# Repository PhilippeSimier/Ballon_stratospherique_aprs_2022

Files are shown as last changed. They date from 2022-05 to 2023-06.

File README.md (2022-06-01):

# Ballon sonde stratosphérique

## Objectifs pédagogiques
La  construction d'une nacelle expérimentale de ballon doit permettre aux jeunes, une découverte des sciences expérimentales. Les expériences  mettent en oeuvre la mesure de grandeurs physiques avec la transmission des données par radiofréquence.  Une initiation à la démarche de projet est aussi proposée.

## Introduction
 L'objectif  est de faire de la science afin de pouvoir mieux comprendre notre atmosphère jusqu’à 30 km d’altitude. Nous tenterons de répondre à la question suivante :

 - Dans quelle mesure l'atmosphère nous protège t-elle du [rayonnement cosmiques](https://www.sievert-system.org/#Rayonnement)   ?

Le rayonnement cosmique est formé de particules qui se déplacent à une vitesse proche de celle de la lumière. Il est constitué de deux composantes, l’une stable, d’origine galactique, l’autre plus fluctuante, liée à l’activité du soleil.
Pour le comprendre, commençons par l'espace lointain. Les rayons cosmiques sont essentiellement des débris subatomiques d'étoiles mourantes, accélérés à une vitesse proche de la lumière par des explosions de supernova. Ils voyagent à travers l'espace et s'approchent de la Terre
dans toutes les directions, bombardant notre planète 24h/24 et 7j/7.
Lorsque les rayons cosmiques s'écrasent dans l'atmosphère terrestre, ils produisent un jet de particules secondaires et de photons qui est le plus intense à l'entrée de la stratosphère. Les physiciens Eric Regener et Georg Pfotzer ont découvert ce maximum en utilisant des ballons dans les années 1930 et c'est ce que nous allons vérifier aujourd'hui.

|Altitude (m)|  Débit de dose (μSv/h)|
|--|--|
|80  | 0.08 |
|5000  | 1.8 |
|8200  | 4.1 |
|10000  | 5.2 |
|11200  | 7.7 |

 [Unité de mesures](https://www.sievert-system.org/#Mesure)

Lors du vol, le ballon traverse une couche appelée le Regener-Pfotzer Maximum, une couche de rayonnement maximal à environ 20 km au-dessus de la surface de la Terre. Ce graphique de rayonnement en fonction du temps pris lors d'un vol en ballon en juillet 2015 illustre le pic :

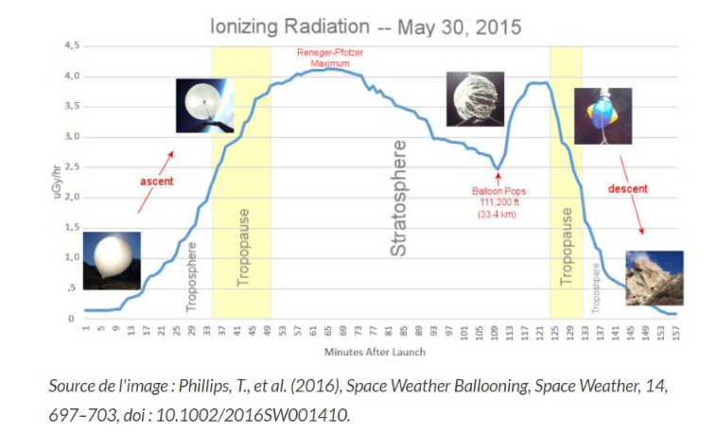
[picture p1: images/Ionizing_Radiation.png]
Ionizing_Radiation


## Principe de la mesure rayonnement ionisant

Le rayonnement est composé de photons gamma et de particules capables de provoquer, directement ou indirectement, la formation d'ions (par arrachement d'électrons) dans la matière qu’ils traversent.

La détection du rayonnement ionisant repose  sur un type particulier de diode, la **diode PIN**. PIN pour Positive Intrisic Negative fait référence directement à la manière dont est constitué le composant.  Dans  une diode PIN on trouve entre les zones P et N une zone non dopée dite intrinsèque.  
La structure PIN permet la détection de photons, un peu à la manière d'un tube Geiger-Muller avec un effet cascade et une brève conductivité. Cela signifie que si un rayon de haute énergie est absorbé, un signal détectable d'électrons est généré. l'absorption photoélectrique est dominante dans la région d'énergie gamma d'intérêt entre 5 keV et 100 keV.
Les détecteurs basés sur **l'absorption directe dans le silicium** constituent une alternative  peu coûteuse par rapport au détecteur à gaz (tube Geiger-Muller).
le capteur utilisé possède une photodiode PIN **[X100-7](https://www.first-sensor.com/cms/upload/datasheets/X100-7_THD_5000040.pdf)** pour la détection des rayons ionisants, ayant une surface de section efficace à grande échelle (100 mm ^ 2), fabriquée par la société **FirstSensor** qui a également fourni un capteur similaire pour le télescope à rayons X de la NASA. En règle générale, l'efficacité du capteur à photodiode PIN est extrêmement stable et ne présente aucune dégradation liée à l'âge.
La détection et l’électronique qui l'entoure est là pour amplifier le signal et le transmettre avec des niveaux adaptés vers un entrée digital de l'ESP32. On obtient le débit de dose par comptage des impulsions sur une periode donnée.

### Principe
Le ballon s’élève dans l’atmosphère grâce à la **poussée d’Archimède**. Plus il monte, plus la pression de l’air autour de lui, diminue. L’hélium occupe alors de plus en plus de volume : le ballon se dilate et finit par éclater.

A ce moment, la chaîne de vol redescend vers la terre. Le parachute inséré initialement «  en sapin  » entre l’enveloppe du ballon et le réflecteur radar, joue alors son rôle de frein.

La durée totale du vol se situe entre 2 et 4 heures. **Planète Sciences** se charge de la demande d’autorisation de vol auprès des autorités. 

### La Nacelle
Pendant le vol, les capteurs seront intégrés dans la Nacelle  qui assurera les fonctions de plate-forme : intégration mécanique, isolation et contrôle thermique, localisation/datation des observations, fourniture de l’énergie grâce à des panneaux solaires et batteries.
La nacelle devra être capable de fonctionner de manière autonome pendant 4 heures, en environnement stratosphérique (pression 50-70 hPa, température environ -80°C).
Les contraintes de masse embarquée sous ballons pressurisés sont telles qu’il est impossible de faire voler une nacelle de plus de 1,8 kg.

### Mécanique 
(design, calculs, atelier, réalisation, intégration) : 
Cette tâche consiste en la conception et la réalisation des coques externes de la  nacelle, ainsi que la structure interne permettant l’intégration des capteurs et des différents sous-systèmes. La structure de la nacelle est réalisée en polystyrène expansé de 30mm d'épaisseur.
La nacelle est recouverte par collage d'une couverture de survie. La colle utilisée est une colle en spray **3M PhotoMount**.

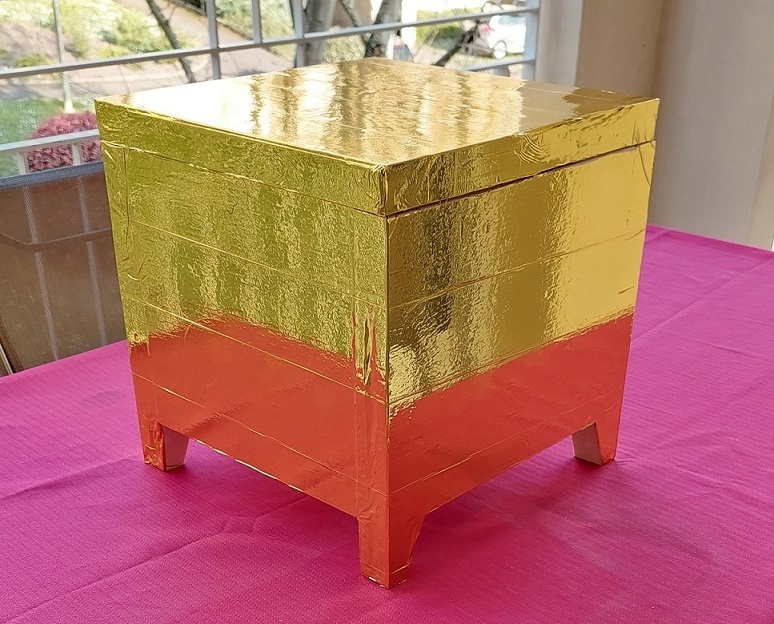
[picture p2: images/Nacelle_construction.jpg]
Nacelle


### Les cartes de télémesures et d'alimentation

L’ensemble des cartes électroniques ont le même format et sont fixées au couvercle. Elles sont ainsi facilement retirables de la nacelle. Les cartes sont empilées  et sont maintenues séparées les unes des autres au moyen de 4 entretoises hexagonales disposées dans les coins. 

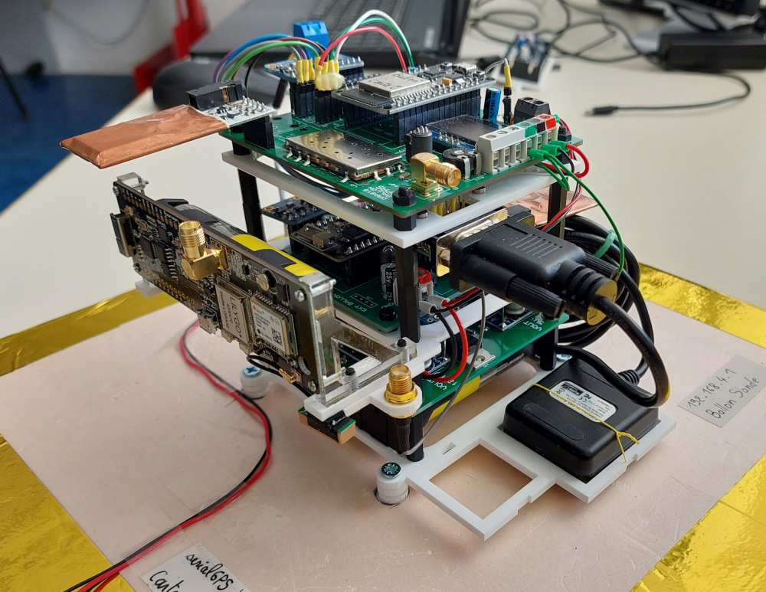
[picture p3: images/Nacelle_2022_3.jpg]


Tout  au  long  du  vol,  les  mesures  sont  enregistrées à bord sur une carte SD. elles  sont aussi envoyées au sol par les émetteurs embarqués (APRS LORA et SIGFOX).

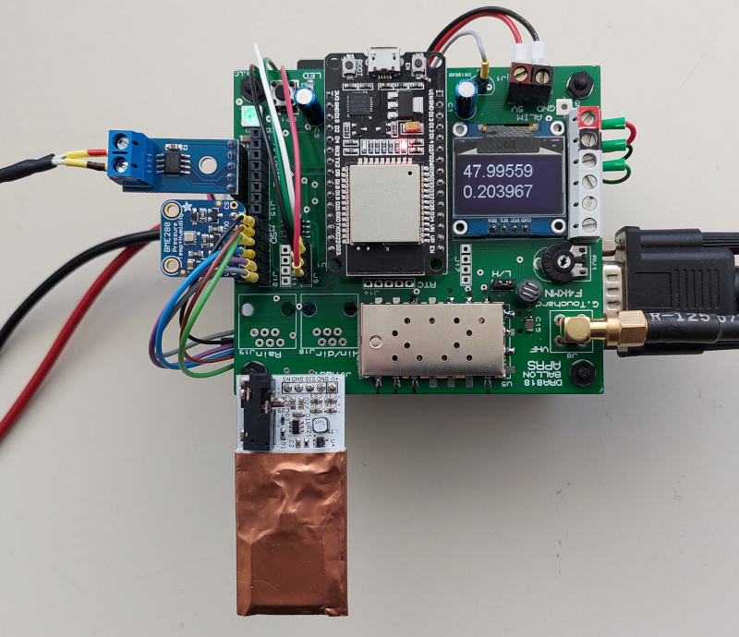
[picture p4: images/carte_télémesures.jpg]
Carte de télémesures


### Le suivi de la trajectoire de vol 

Afin de faciliter la récupération de la nacelle, le système de télémesures est équipé d’un récepteur GPS pouvant fonctionner en haute altitude.
Le suivi du vol est effectué par transmission de la position dans des trames **APRS** encapsulé dans des trames **FX25** et aussi **LoRa**.  
La position est également transmise sur le réseau **SIGFOX**.

La position du ballon ainsi que la télémétrie peuvent être suivie en temps réel sur le site https://aprs.fi/

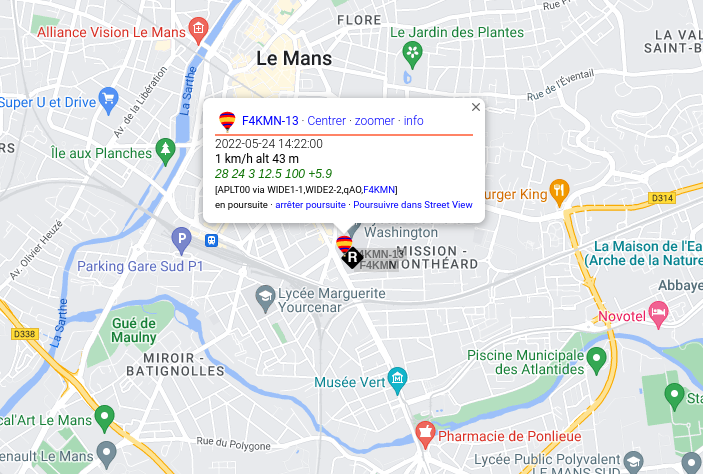
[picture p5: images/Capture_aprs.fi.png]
aprs.fi


ou sur le site https://aprs-map.info/

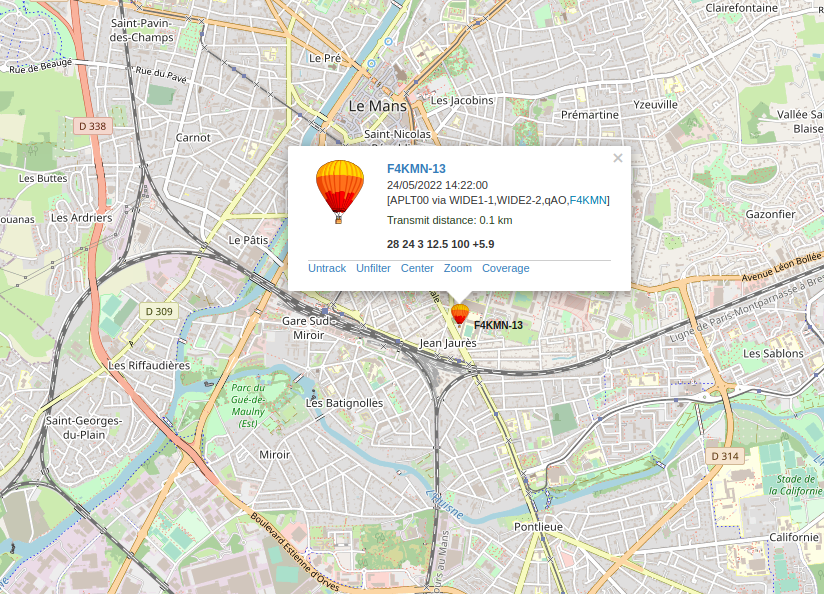
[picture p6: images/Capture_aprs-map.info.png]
aprs-map.info


## La télémétrie

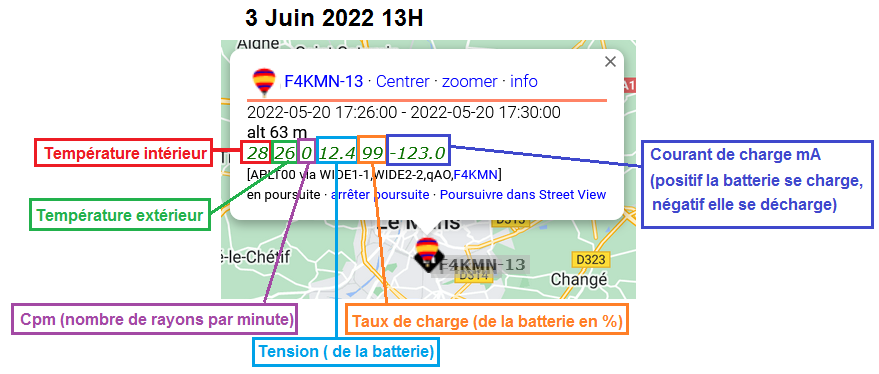
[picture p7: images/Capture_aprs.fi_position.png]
aprs.fi


La télémétrie permet de suivre la charge de la batterie, les températures intérieur et extérieur, le nombre par minute de rayons cosmiques. 

## Les prévisions de trajectoire et météorologiques

[Prévisions de la trajectoire](https://predict.habhub.org/)
[Prévisions météorologiques](https://www.ventusky.com)

Prévision de la trajectoire 48 heures avant le lancement
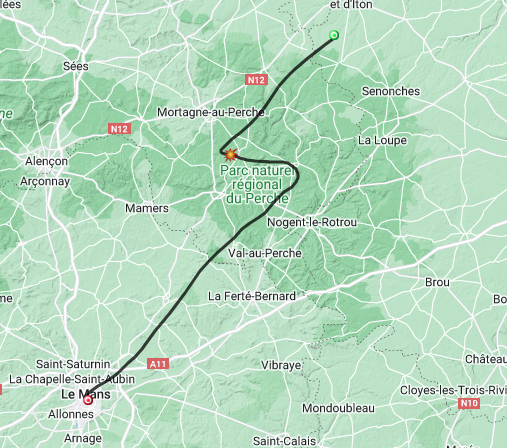
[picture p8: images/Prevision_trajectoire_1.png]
Prévision trajectoire


## Les contraintes

 1. La chaîne de mesure doit être étalonnée dans son intégralité     (système au sol compris) avant le vol.

 2. L'alimentation de la chaîne de mesure doit posséder une autonomie supérieure à 4 heures.

 3. La localisation se fait alors par l'écoute d'une des _fréquences_ utilisées par  _Planète Sciences_ ( 137.05 MHz ).

Section Système Numérique Informatique & Réseaux

Logo Lycée Touchard Logo CNES
Logo Planete sciences

<!-- Toolbox
Génération du README  https://stackedit.io/app#
Génération des badges https://shields.io/category/build

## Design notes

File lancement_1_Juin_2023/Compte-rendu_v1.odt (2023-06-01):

Pesage de la nacelle 1626 g

alimentation

consommation 247mA

Taux de charge de la batterie restant 70 %

tension 11,7 V

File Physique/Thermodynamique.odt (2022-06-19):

## Thermodynamique

Système Nacelle

Travail

W

Transfert thermique
Q

Sources électriques Air ambiant

Variation d’énergie interne du sytème

%DELTA U_système = W +Q

La température interne de la nacelle avant le décollage est constante donc %DELTA U _système = 0

La nacelle est composée de panneau en polystyrène extrudé épaisseur 30mm

Le constructeur donne la résistance thermique pour 1 m² de panneau : 0,90 m²KW⁻¹

Surface intérieure des 6 faces 0,24 * 0,24 * 6 = 0,3456 m²

Rth = 0,90 / 0,3456 = 2,6 KW⁻¹ R_{ th } = {0,90} over {0,3456} = bold 2,6 KW ^{-1}

à 13h43 la nacelle est fermée la température intérieure est constante.

%theta_{i} = 34 °C
%theta_{ext} = 24 °C
%DELTA %theta = %theta_{e} - %theta_{i} = -10 °C

Flux thermique %PHI = {%DELTA %theta} over { R_{th} } = { -10 } over { 2,6 } = bold -3,84 W

Puissance électrique dissipée par les cartes électronique APRS et Sigfox = 12,4 * 0,174 = 2,15 W

Puissance électrique carte ttgo LoRa 4.00V * 102mA = 0,408 W

Puissance électrique GoPro 5V * 250mA = 1,25 W

Total puissance électrique = 3,8 W

Bilan des puissances Pe + flux thermique 3,8 – 3,84 = - 0,04W

Conclusion le bilan des puissances est équilibré

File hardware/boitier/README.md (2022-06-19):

# Conception Mécanique

## Liens utiles

**Conception 3D** 

https://www.tinkercad.com/dashboard

**Converter svg to dxf**

https://cloudconvert.com/svg-to-dxf

**Viewer dxf de autodesk**

https://viewer.autodesk.com/designviews

# Assemblage nacelle

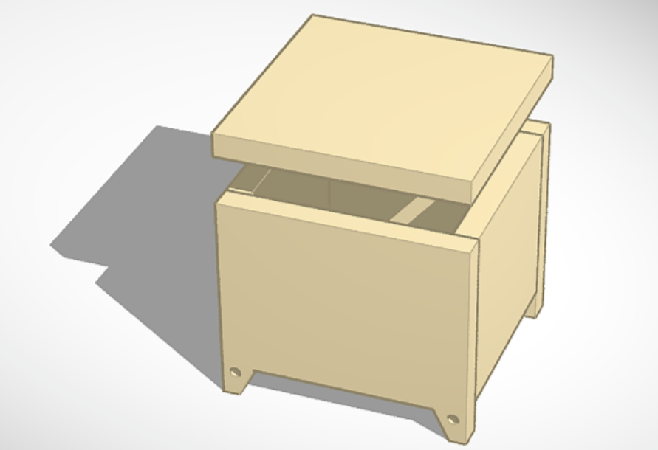
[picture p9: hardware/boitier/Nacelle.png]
Assemblage nacelle


# Les piéces mécaniques

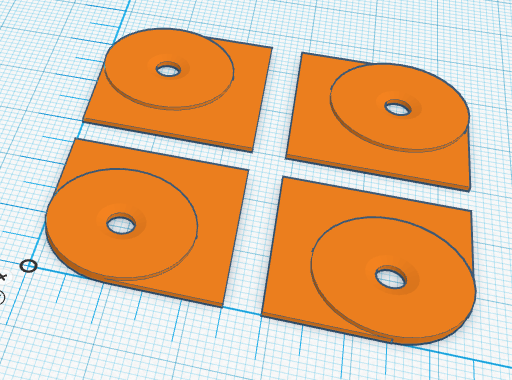
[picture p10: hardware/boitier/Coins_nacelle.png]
coins nacelle


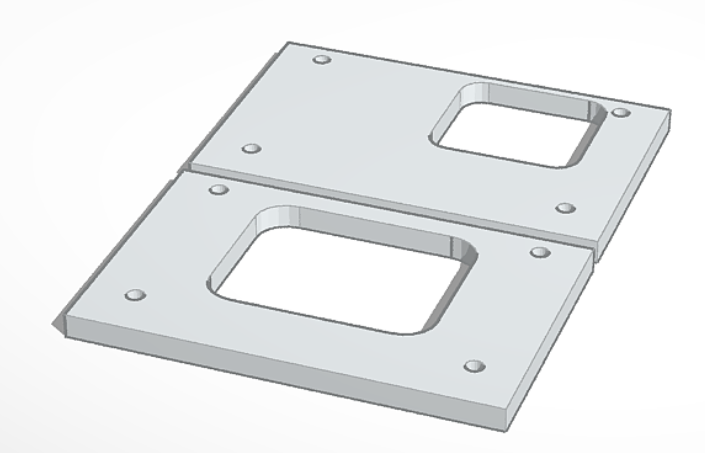
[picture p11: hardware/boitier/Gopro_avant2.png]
Gopro_avant2


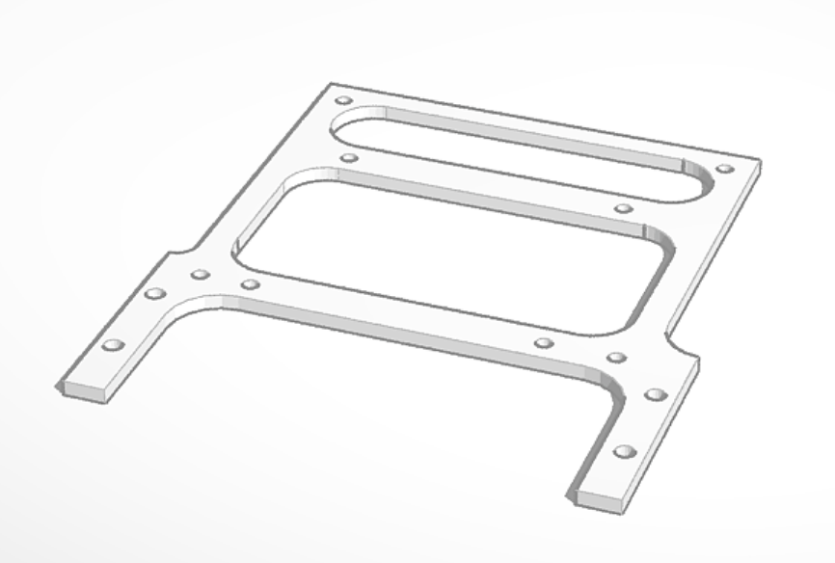
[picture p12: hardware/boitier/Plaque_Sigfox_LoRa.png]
Plaque_Sigfox_LoRa


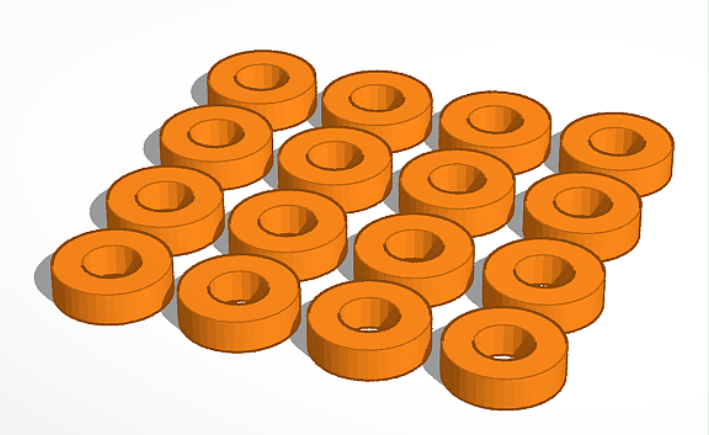
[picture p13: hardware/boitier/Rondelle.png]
Rondelle


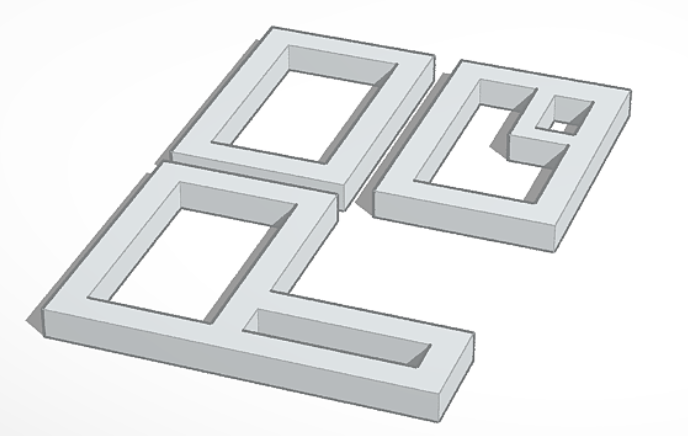
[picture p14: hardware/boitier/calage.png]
calage


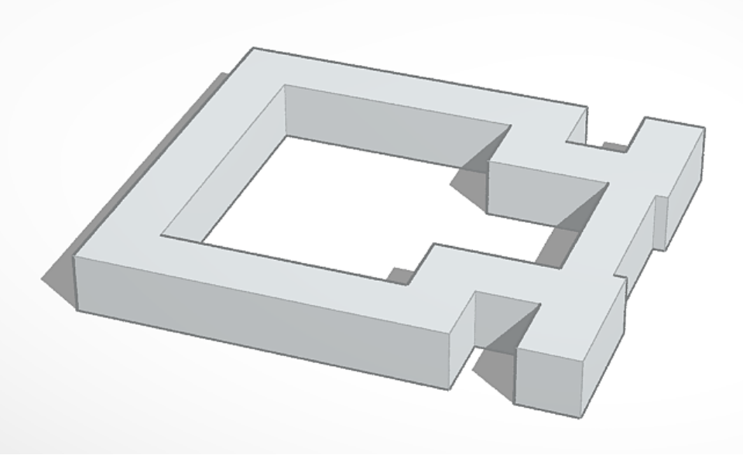
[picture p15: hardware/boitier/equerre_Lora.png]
équerre LoRa


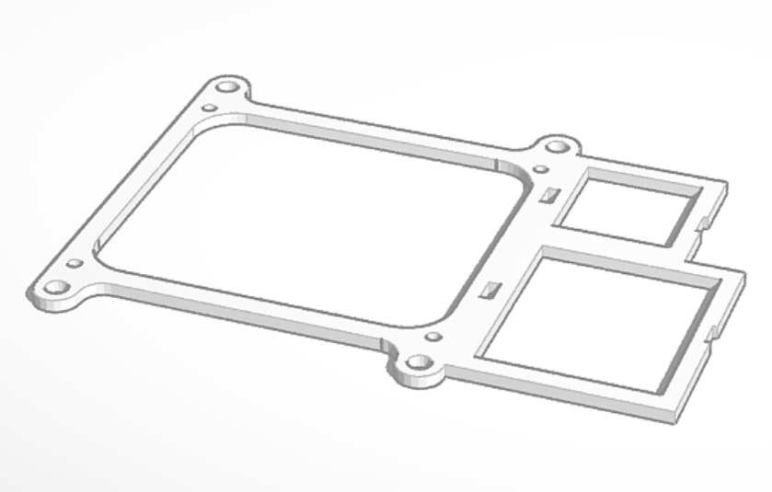
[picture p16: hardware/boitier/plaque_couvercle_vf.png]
plaque couvercle


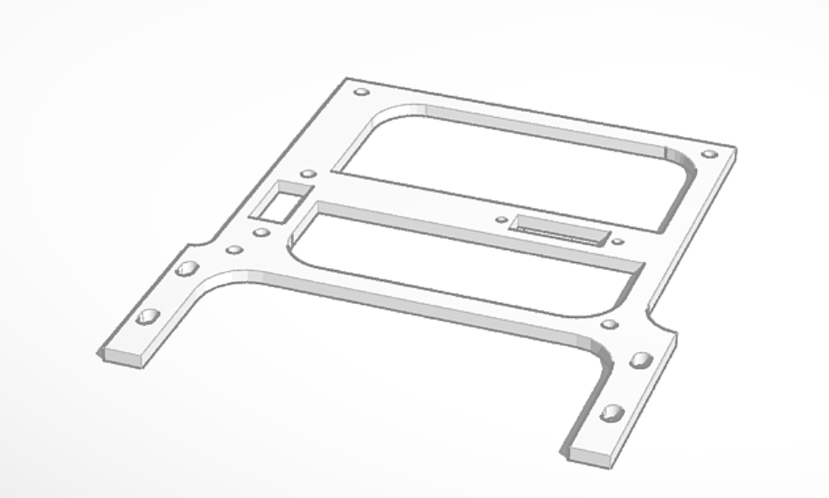
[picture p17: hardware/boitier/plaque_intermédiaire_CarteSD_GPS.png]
plaque carte SD & GPS


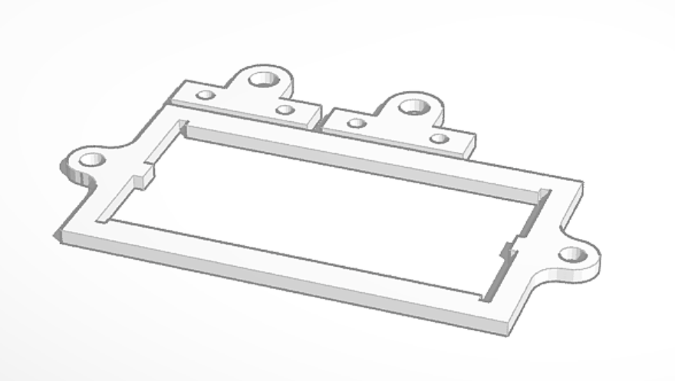
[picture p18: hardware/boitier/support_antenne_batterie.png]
support antenne batterie gopro


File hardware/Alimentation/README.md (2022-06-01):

# Génération d'énergie

## Objectif

La  _génération d'énergie_  permet le fonctionnement de la nacelle en lui fournissant l'énergie électrique dont elle a besoin. En effet, cette dernière étant mobile et autonome, elle a besoin de produire son électricité. Le système d'alimentation électrique est découpé en quatre éléments qui sont la production (ou **source primaire**), le stockage (ou **source secondaire**), la régulation et la distribution.

-   La production électrique utilise  le flux solaire grâce à des panneaux solaires placés sur les côtés de la nacelle.  Des cellules solaires assurent la conversion de l'énergie lumineuse en énergie électrique, avec un certain rendement entre 20 et 30% . 
-   L'énergie produite est ensuite stockée dans les batteries 18650 (lithium ion) afin d'alimenter la nacelle lors des phases  ou la consommation instantanée est supérieure à la production des panneaux.
-   La régulation et la distribution permettent de fournir aux éléments nécessitant de l'énergie une alimentation présentant des caractéristiques électriques précises et compatibles. La régulation permet de garantir la durée de vie de la batterie. Pour ce faire, on limite la profondeur de décharge, c'est-à-dire la quantité d'énergie fournie par la batterie.
- Par ailleurs on coupe le courant de charge lorsque la température intérieure dans la nacelle est inférieur à 0°C.

## Schéma

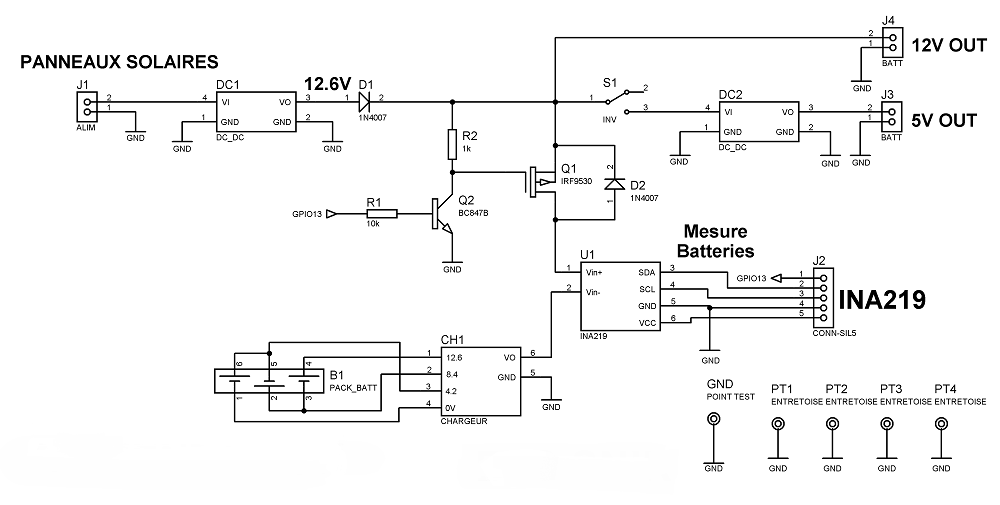
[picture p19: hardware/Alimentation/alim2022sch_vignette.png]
schema alimentation
 

 ## PCB
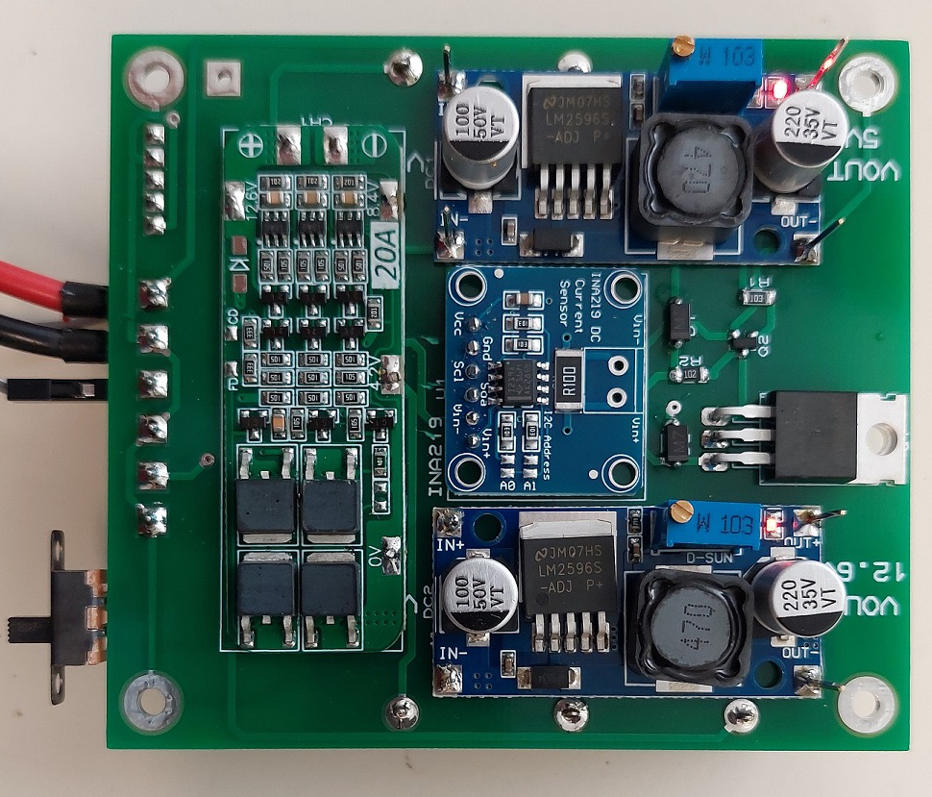
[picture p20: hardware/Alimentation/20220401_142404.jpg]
carte coté composants
 

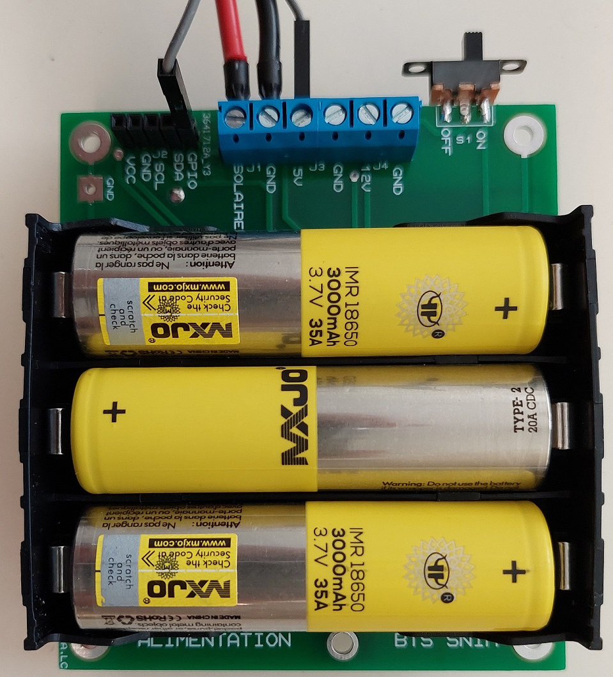
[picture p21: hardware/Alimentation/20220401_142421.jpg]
carte coté batteries


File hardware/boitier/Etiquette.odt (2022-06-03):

Cet objet est inoffensif.

Il est la propriété du

Cet objet est la concrétisation d'un projet d'élèves. Nous sommes en route pour le récupérer.

Si vous le trouvez merci d'appeler le :

07 68 12 72 54

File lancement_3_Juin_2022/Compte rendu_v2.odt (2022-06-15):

# Ballon stratosphérique Lycée Touchard Washington

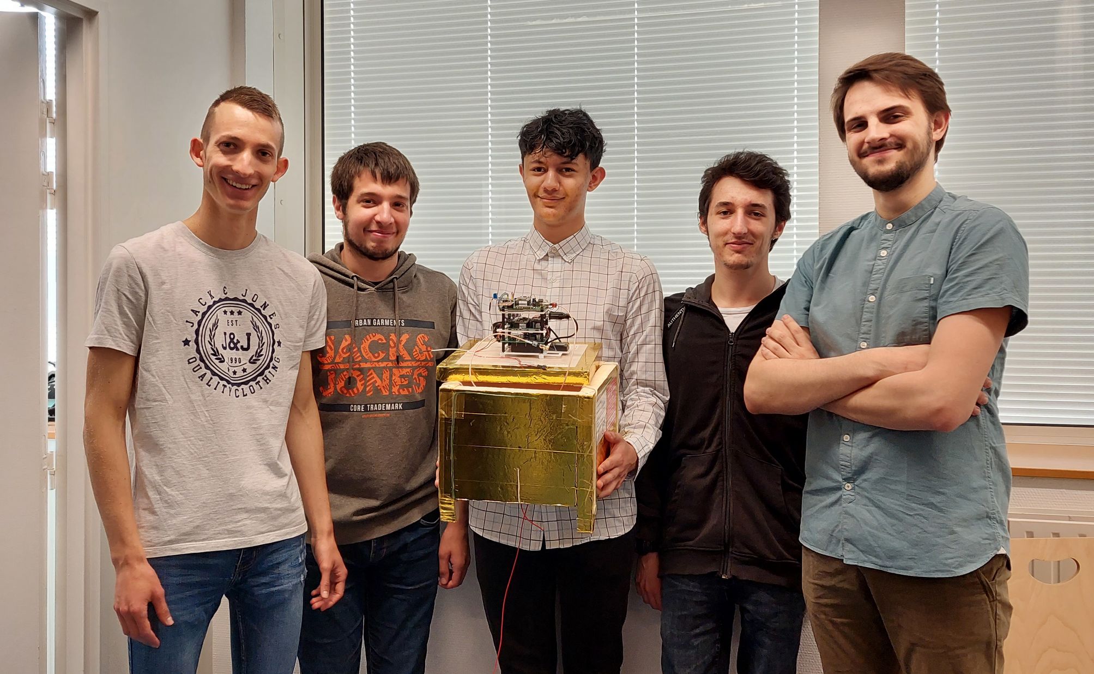
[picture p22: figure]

Desaunay Valentin, Neveu Benjamin, Suard Mickael , Maillard Clement, Porcheron Enzo

Professeurs référents : Bernard Didier, Le Cren Anthony, Simier Philippe

# Bilan des mesures Ballon 2022

### Présentation générale

Le projet de ballon stratosphérique 2022, fut réalisé par 5 étudiants dans le cadre du projet de deuxième année du BTS Système numérique option informatique, durant l'année scolaire 2021-2022. Les idées motivant sa réalisation étaient la mesure de la radioactivité en altitude et l'utilisation d'un capteur GNSS pour suivre la position du ballon, et donc le récupérer. Le ballon a été lancée le 3 juin 2022 depuis Le Mans (72), suivi par une voiture et retrouvé quelques minutes après son atterrissage. Malgré quelques problèmes, les résultats des expériences ont pu être exploités avec intérêt.

### Pesée - Vitesse de montée - Altitude d’éclatement

Le ballon s’élève dans l’atmosphère grâce à la poussée d’Archimède. Plus il monte, plus la pression de l’air autour de lui, diminue. L’hélium occupe alors de plus en plus de volume : le ballon se dilate et finit par éclater.

A ce moment, la chaîne de vol redescend vers la terre. Le parachute inséré initialement « en sapin » entre l’enveloppe du ballon et le réflecteur radar, joue alors son rôle de frein.

Masse de la nacelle : 1455 g.

Nous sommes en dessous des 1800 g exigé par le cahier des charge. Le gonflage du ballon a été adapté (5,1 m³ d’hélium) afin d’avoir la portance qui permette une vitesse ascensionnelle de 5 m/s.

Vitesse ascensionnelle décollage = 4,74 m/s

Vitesse ascensionnelle à 4000 m = 5,21 m/s

Vitesse ascensionnelle à 20000 m = 5,41 m/s

Vitesse ascensionnelle à 30000 m = 6,57 m/s

Altitude à l’éclatement = 34 295 m

Les années précédentes la nacelle était plus lourde (1800g) le ballon était donc gonflé avec un volume d’hélium plus important et éclatait vers 30 000m. Conclusion , un ballon contenant moins d'hélium éclate à une altitude plus élevée.

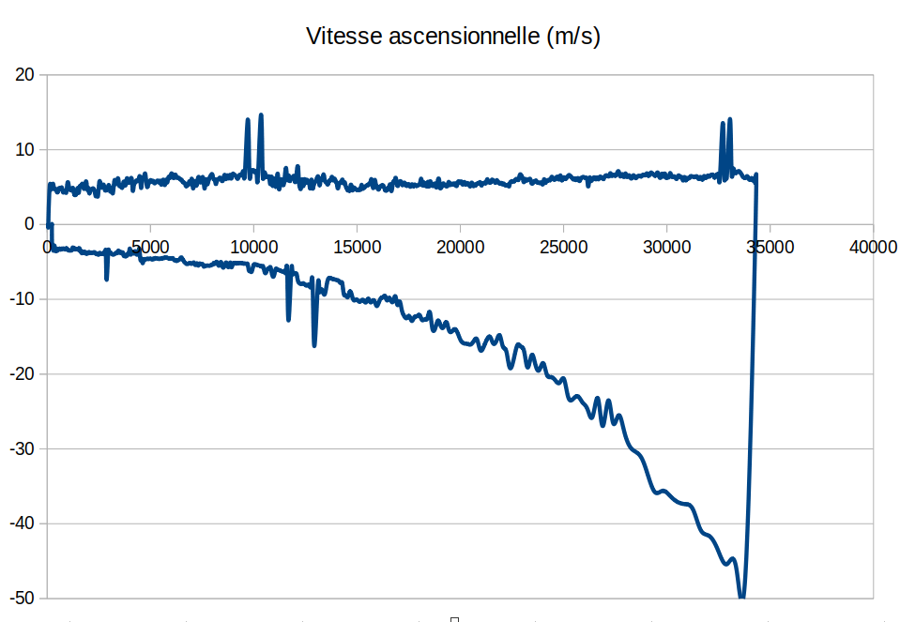
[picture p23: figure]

Descente

Montée

On remarque une vitesse de montée presque constante, entre 5 m/s et 6 m/s, et une vitesse de descente qui suit bien celle de la masse volumique de l'air.

### Alimentations

L'alimentation de la charge utile du ballon est une des parties essentielles pour le succès du projet. Elle est loin d’être évidente à concevoir et peut mener à l’échec total du projet. La conception doit prendre en compte plusieurs contraintes :

- La masse limitée de la charge utile, ce qui oblige à limiter le nombre d’accumulateur et à surveiller leur taux de charge.
- Le courant de pointe, alimenter de électronique d'instrumentation et un émetteur à partir de la même source n'est pas évident.
- Les conditions de température, les caractéristiques des accus n’étant pas trop documentées à

température ambiante, elles sont inconnues aux très basses températures.

Bilan électrique

Les cartes doivent être alimentées avec une

- Tension d’alimentation 5V
- Consommation 170 mA (250mA avec l’émetteur du WIFI).

Réalisation

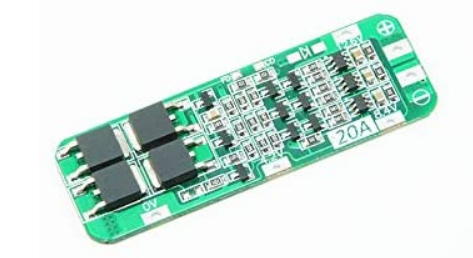
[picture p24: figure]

Trois accumulateurs 18650 (lithium ion) de capacité 3000 mAh sont utilisées. Leur tension nominale est 3,6 V. Ils sont montés en série. La tension au bornes de l’ensemble atteint 12,6 V lorsqu’ils sont complètement chargés et 9,6 V lorsqu’ils sont déchargés.

Le travail de surveillance est effectué grâce à une carte électronique de gestion appelée BMS “Battery Management System”.

Le BMS interrompt la décharge des cellules avant que cela ne devienne critique pour leur durée de vie.

  Il interrompt aussi la charge des cellules avant qu’elles ne soient trop chargées
  Il optimise un chargement homogène d’une cellule à l’autre
  Il vérifie la température des cellules.

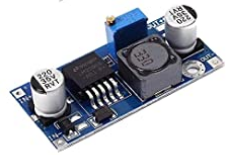
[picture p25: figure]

un convertisseur DC DC buck, (hacheur série) abaisse la tension à 5v.

Le capteur INA219 est aussi utilisé pour mesurée le courant et la tension. Il est donc possible de connaître en temps réel l’état de charge des accumulateurs grâce au calcul du SOC “State Of Charge” en %

En définitive une carte spécifique a été développée pour connecter l’ensemble des éléments.

Avant le lancement la charge des batteries est maintenue à l’aide d’une alimentation nourrice extérieure à la nacelle. Juste avant le lancement la nourrice est déconnectée. la tension au décollage était de 12,6 V à la fin du vol 12V, la charge restante était de 2393 mAh soit un taux de charge de 79 %.

L’alimentation à parfaitement remplit sa fonction.

### Fréquences et Indicatifs des émetteurs

La nacelle est équipée de trois émetteurs radios:

- APRS sur LoRa fréquence 433,775 MHz indicatif F4KMN-11
- APRS sur FX25 fréquence 137,05 MHz indicatif F4KMN-13
- Sigfox fréquence 868 MHz indicatif C50EE9
  Les émissions sont décalées
- trame APR FX25 à la seconde 57
- trame APRS Lora à la seconde 10
- trame Sigfox à la seconde 40

### Le suivi de la trajectoire

Le taux de mise à jour pour le suivi est d'une fois par minute sur la fréquence 433 MHz (Lora) et d’une fois toutes les deux minutes pour les fréquences 137,05 MHz (APRS FX25) et 868 MHz (Sigfox).

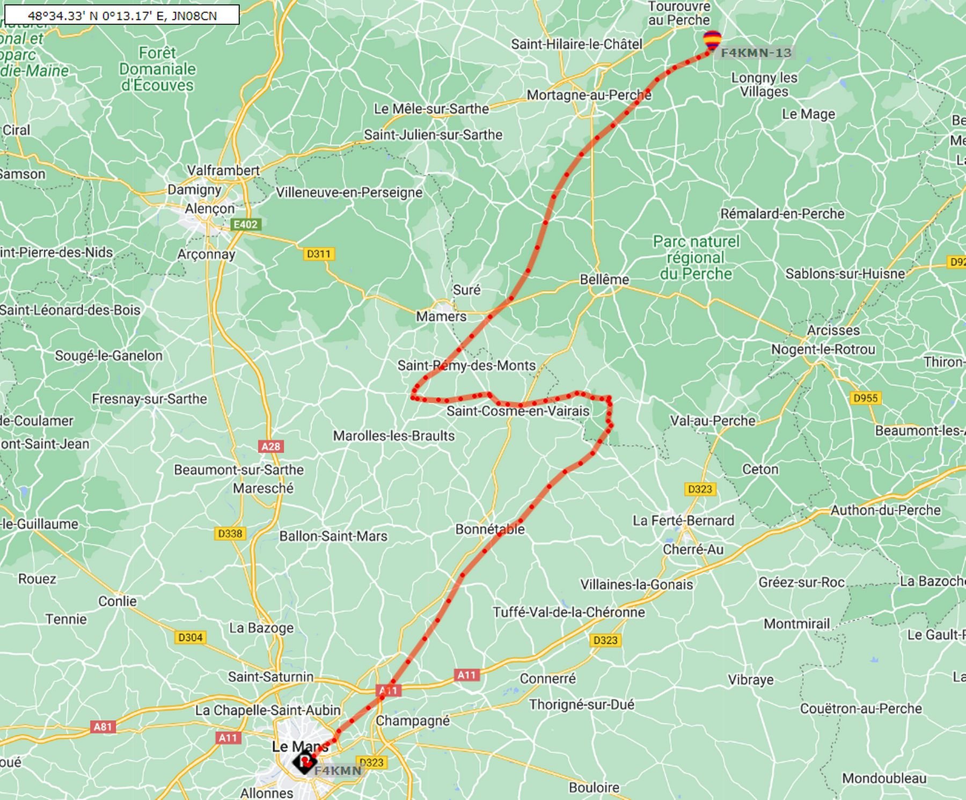
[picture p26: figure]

Temps de vol

Départ 13h 44' 15'' Arrivée 16h 29' 55'' durée 2h 45' 40''

Sur la carte TTGO « LoRa », la puce GNSS a cessé de fonctionner à une altitude d'environ 12 000 m. Les positions du ballon au-dessus de 12 000 m était donc totalement fausse. Cependant le fonctionnement est revenu à la normale à la descente. On remarque que les points sont plus serrés que sur la trajectoire précédente car le taux de mise à jour est de une toute les minutes.

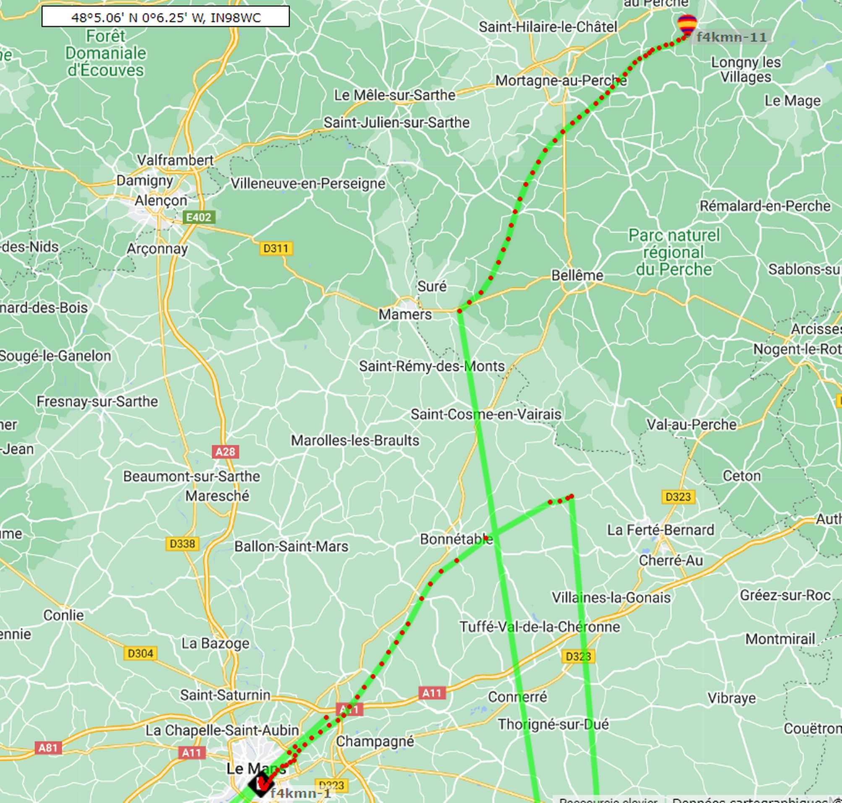
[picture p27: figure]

Après quelques recherches sur le WEB, nous découvrons que la puce GNSS (NEO-6M) est configurée par défaut sur le modèle de plate-forme dynamique Portable (altitude max 12000m). Toutefois elle peut enregistrer les rapports d'altitude et de positionnement jusqu'à 160 000 FT (48 768 m), nous devons nous assurer d'activer le modèle de plate-forme dynamique (voir tableau ci-dessous) pour ajuster le moteur de navigation à l'environnement d'application attendu. le modèle Airborne1g est prévu pour fonctionner jusqu'à 50 km d'altitude.

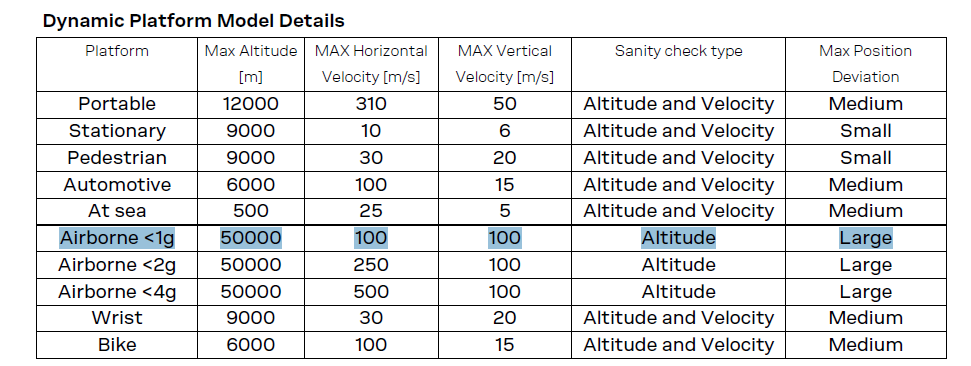
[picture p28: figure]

Vitesse mesurée de descente après éclatement

13941 pieds = 4249 m 4249 / 120 = 35,40 m/s 127 km/h

Le modèle Airborne <1g est prévu pour fonctionner jusqu'à une vitesse verticale de 100m/s.

Conclusion

Le modèle Airborne <1g est le mieux adapté.

Par contre quand le ballon est retombé au sol, il serait bien de revenir au modèle Stationary qui donne la meilleur précision de position possible.

Extrait de programme pour adapter le modèle

myGPS.setDynamicModel(DYN_MODEL_AIRBORNE1g);

// Verification de la prise en compte

uint8_t newDynamicModel = myGPS.getDynamicModel();

if (newDynamicModel == 255)

{

Serial.println(F("***!!! Warning: getDynamicModel failed !!!***"));

}

else

{

Serial.print(F("The new dynamic model is: "));

Serial.println(newDynamicModel);

}

### La mesure des radiations

L'expérience principale consiste à mesurer la radioactivité en altitude, ce qui présente plusieurs difficultés. Divers capteurs sont possibles, mais les contraintes de masses et de coût limitent énormément les possibilités. En définitive, nous avons fait au plus simple, en choisissant un compteur Geiger du commerce, ce qui permet de mesurer le flux de particules d'une certaine énergie dans l'élément sensible. Le compteur, choisi pour son coût, sa simplicité et sa disponibilité, est un modèle radiation watch. (Plage de mesure de 0,05 uSv/h à 10 mSv/h entre 0,01 cpm et 300 Kcpm)

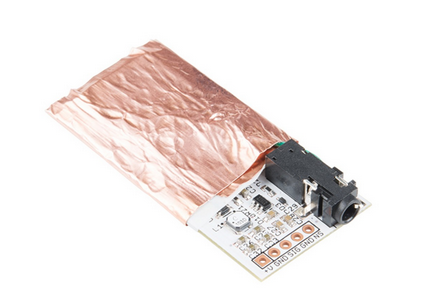
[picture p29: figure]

Le rayonnement est composé de photons gamma et de particules capables de provoquer, directement ou indirectement, la formation d'ions (par arrachement d'électrons) dans la matière qu’ils traversent.

La détection du rayonnement ionisant repose sur un type particulier de diode, la diode PIN. PIN pour Positive Intrisic Negative fait référence directement à la manière dont est constitué le composant. Dans une diode PIN on trouve entre les zones P et N une zone non dopée dite intrinsèque.
La structure PIN permet la détection de photons, un peu à la manière d'un tube Geiger-Muller avec un effet cascade et une brève conductivité. Cela signifie que si un rayon de haute énergie est absorbé, un signal détectable d'électrons est généré. l'absorption photoélectrique est dominante dans la région d'énergie gamma d'intérêt entre 5 keV et 100 keV. Les détecteurs basés sur l'absorption directe dans le silicium constituent une alternative peu coûteuse par rapport au détecteur à gaz (tube Geiger-Muller).

Notre expérience vise à confirmer les données concernant le maximum Regener-Pfotzer. Nous n'avons trouvé aucune étude européenne sur le maximum de Regener-Pfotzer lors de nos recherches.

Lors de nos mesures nous avons constaté un maximum à 69369 pieds = 21 143 m → 107 cpm

La dose de rayonnement diminue comme prévu lorsque le capteur atteint des altitudes plus élevées que ce Maximum dit de Regener-Pfotzer .

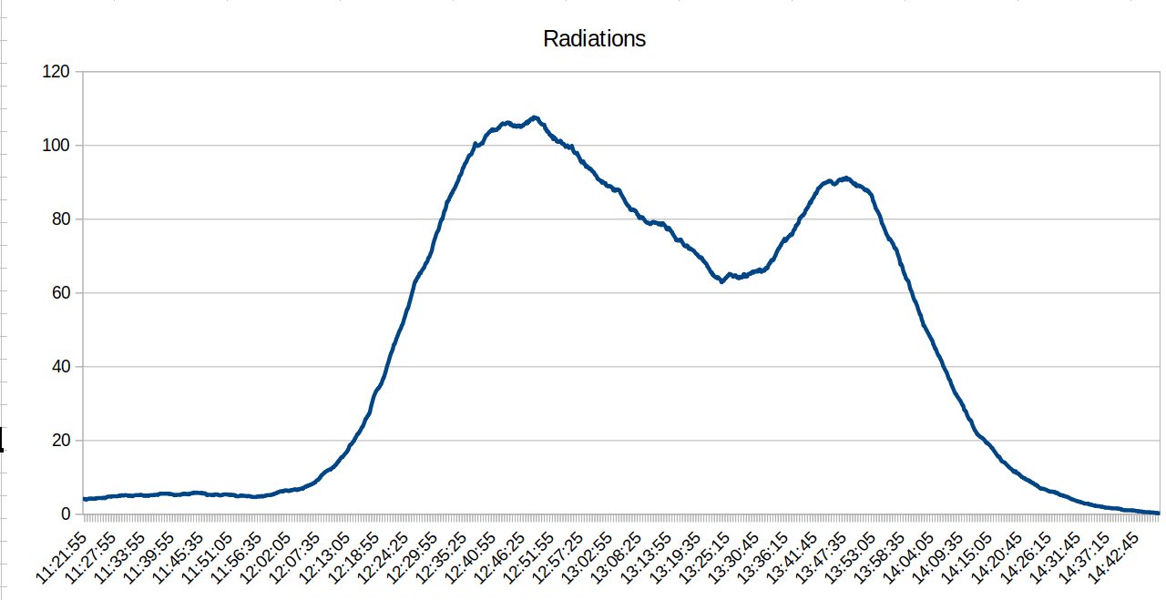
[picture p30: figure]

Regener-Pfotzer Maximum

Lancement

éclatement

ascension

descente

Cpm

temps

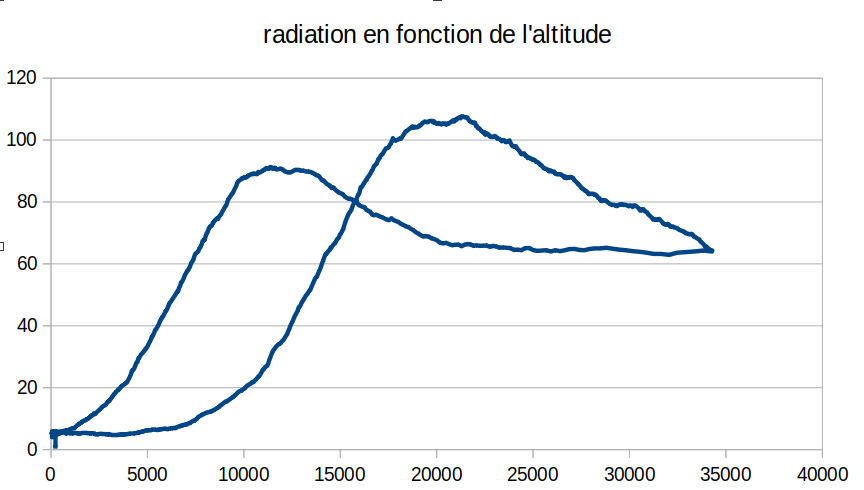
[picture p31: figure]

Conclusion : Nous observons bien un maximum pour l'altitude 20000m. La hausse due au rayonnement apparaît plus tardivement lors de la descente, car la vitesse de descente est plus importante que celle de la montée à ces altitudes.

### Evolution de la température avec l'altitude

La température extérieure est mesurée par un thermocouple de type K (Plage :-100°C à 500°C ). La difficulté dans l’utilisation du thermocouple est que la tension à mesurer est très faible, avec des variations d'environ 50 uV par °C avec une compensation de température froide. Pour toutes ces raisons, nous utilisons une puce d'interface MAX31855 qui fera le gros du travail, nous permettant d'intégrer facilement le capteur sans trop de difficulté.

La température minimale a été atteinte à 37355 pieds = 11 385 m → -45 °C

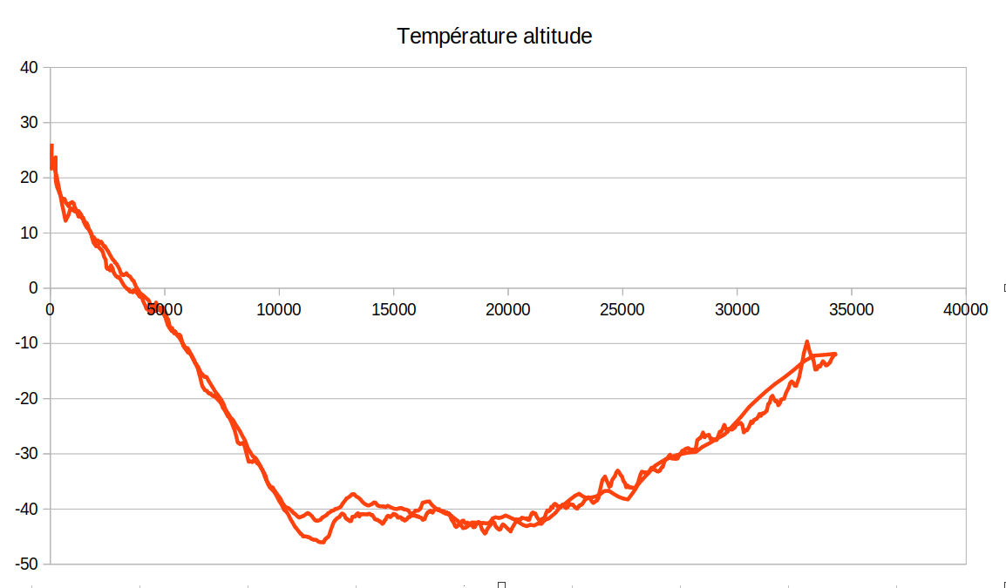
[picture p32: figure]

Altitude (m)

Température °C

-45

-11 385

Troposphère

Tropopause

Stratosphère

Le gradient thermique dans la troposphère est : -5,9 °C/Km

Le gradient thermique dans la tropopause est : +0 °C/km

Le gradient thermique dans la stratosphère est : +2,22 °C/km

Conclusion les valeurs de température mesurée avec le thermocouple de type K sont proches des valeurs de l'atmosphère standard dite «ISA» (International Standard Atmosphere)

### Température minimale à l’intérieur de la nacelle

Un capteur mesure la température à l'intérieur de la nacelle. L’objectif est d’avoir une température positive à l’intérieur de la nacelle pendant toutes les phases du vol.

La température minimale est de +2,2 °C obtenue pendant la descente à 7000m d'altitude.


Eclatement

Montée

Descente

La nacelle s’est refroidie pendant la montée jusqu'à 22000m, puis elle s’est réchauffée. En descente, au environ de 7000m la température minimale est atteinte. Il y a donc eu un refroidissement continu de la nacelle par conduction thermique.

Les hausses de température observées dans les altitudes basses et hautes sont sûrement dues aux

transferts de chaleur par rayonnement infra-rouge.

La couverture de survie est revêtue de deux faces métallisées distinctes, respectivement dorée et argentée. Ces faces répondent à deux fonctions distinctes : le côté argenté, initialement développé par la Nasa, réfléchit 90% du rayonnement infrarouge, tandis que le côté doré absorbe 50% de la chaleur incidente. De ce fait, en positionnant la face dorée vers l'extérieur, la nacelle est protégée du froid, en retenant sa chaleur.

### Evolution de la pression avec l'altitude


Pression (hPa)

Altitude (m)

La pression est réduite :

- d'un facteur 2 à l'altitude 5500 m (513 hPa)
- d'un facteur 10 à 16547m (100 hPa).

Ces mesures sont conformes au t (https://fr.wikipedia.org/wiki/Variation_de_la_pression_atmosphérique_avec_l%27altitude)ableau de la pression atmosphérique nominale selon l'altitude (https://fr.wikipedia.org/wiki/Variation_de_la_pression_atmosphérique_avec_l%27altitude), dans la troposphère.

### Trames APRS via LoRA

Pendant le vol, une trame par minute est émise, soit au total 177 trames transmises.

Les trames ont été entendues et relayées par les relais suivants.


Nombre de trames relayées par station (grep F1ZCK-10 Trame_F4KMN-11.txt | wc)

F1ZCK-10 | 324 | F4GXP-10 | 5
F4ECA-10 | 304 | ON5YW-15 | 4
F4KMN-1 | 163 | HB9TQJ-3 | 4
F4GOH-1 | 122 | ON3CRX-10 | 3
F4GXP-5 | 93 | ON7WP-11 | 2
F4HVU-10 | 72 | F4EWJ-10 | 2
F1ZIF-10 | 46 | DB0MOE-10 | 2
F8GHE-10 | 45 | ON7KY-12 | 2
DB0WTH-12 | 27 | ON8SV-15 | 2
DF7RW-2 | 19 | ON8BZ-13 | 1
DB0HRW-10 | 15 | ON7KY-11 | 1
F4DVK-10 | 14 | DB0NOR | 1
F5RVX-10 | 11 | DB0WK-10 | 1
ON4JPS-10 | 8 | ON3MPE-10 | 1
ON7TA-10 | 7 | F4GXP-3 | 1

Remarque : Les Relais F1ZCK-10 et F4ECA-10 ont bouclé sur eux-mêmes, ce qui explique qu’ils ont entendu plus de messages que le ballon en a envoyés.

### Atterrissage

Le véhicule suiveur à emprunté l’autoroute ; il est arrivé à proximité du point de chute prévisionnel environ 30 minutes avant l’atterrissage. Finalement, le véhicule suiveur est arrivé sur la zone du point du chute à 16h32 deux minutes après l’atterrissage (16h30). La poursuite du ballon a donc été un succès.

La charge utile avec le réflecteur et le parachute se sont posé sur une petite route de campagne.

route de l’épine Jousset

commune de Tourouvre au Perche dans l’Orne

Latitude : 48,562312° Longitude: 0,684471° heure 16h 29' 55''


Son état général est très bon, les cartes n’ont pas bougé, seule la plaque de fixation de la carte TTGO a cédé à l’impact.


Il faudrait modifier la fixation de cette carte afin d’avoir 4 points d’accrochage !

Il faudrait aussi renforcer les pieds de la nacelle.

### Logiciels Github

Les programmes informatiques sont disponibles sur les dépôts Github des étudiants et des professeurs.

Programme serveur web Valentin Desaunay (https://github.com/ValentinDesaunay/Projet_Ballon_2022)

Programme carte Sigfox Benjamin (https://github.com/BenjaminNeveu/Ballon_sonde) (https://github.com/BenjaminNeveu/Ballon_sonde)Neveu (https://github.com/BenjaminNeveu/Ballon_sonde)

Programme carte APRS Lora & iGate F4GOH (https://github.com/f4goh/lora-aprs-esp32)

Programme carte APRS FX25 Philippe Simier (https://github.com/PhilippeSimier/Ballon_stratospherique_aprs_2022)

### Conclusions générales

Pour conclure, nous pouvons maintenant répondre aux questions que nous nous sommes posées au début de notre projet. Le flux de rayonnement augmente-t-il réellement en altitude et, si tel est le cas, la différence de niveaux de rayonnement est-elle suffisamment importante pour constituer une menace pour les humains ?

Nous avons pu constater qu'il y a une augmentation constante du rayonnement à mesure que l'altitude augmente en raison de l'effet de protection de l'atmosphère, jusqu'à une hauteur d'environ 20 km où le rayonnement cosmique secondaire est le plus intense en raison de la formation des cascades de particules.

Le ballon a occupé une place importante pour nous tous et durant toute une année. L'organisation de projet, les connaissances théoriques acquises, les difficultés levées et le savoir-faire développé marquent déjà le projet d'une très grande réussite.

Après de nombreuses péripéties, le ballon a pu prendre son envol. Malgré quelques difficultés les résultats obtenus sont intéressants et en tout cas confirment le succès technique du projet.

Compte rendu du lancement ballon du 3 juin 2022 Lycée Touchard le Mans page 17/17

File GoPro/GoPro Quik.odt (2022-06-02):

# Commande de la Gopro

Notre besoin est de contrôler la caméra GoPro à distance pour obtenir le démarrage de la vidéo au moment du lancement du ballon.

De cette façon il est possible de fermer le couvercle de la nacelle bien avant le lancement

## Un téléphone comme télécommande pour votre GoPro.

L'application GoPro Quik est disponible pour les smartphones Android.

Grâce à cette application, il est possible d’ajuster les réglages de la vidéo (format et le nombre d'image par seconde, 1080p à 30 ips). On a en direct le retour vidéo de la GoPro. Cette fonctionnalité est idéale pour s'assurer du bon fonctionnement de la camera GoPro .

De plus grâce à cette application, on peut aussi lire, modifier et effacer les fichiers présents sur la carte micro SD.

## Installation de l'application GoPro Quik


sur le Play Store rechercher gopro quik

installer l'application puis l'ouvrir

## Contrôler la GoPro


Activer le bluetooth sur le téléphone

Allumer la camera avec un appui sur le bouton Mode situé sur le côté, trois bips sont émis, l'écran s'allume.

- Lancer l'application Quik sur le téléphone
- Sur la camera, ouvrez l'onglet de connexion en balayant du haut vers le bas le doigt sur l'écran tactile.
- Puis cliquer sur CONNECTER
- Sélectionner Connecter nouv périph
- Sur l'écran du téléphone cliquer sur Contrôler votre GoPro
  Soyez patient La connexion demande une vingtaine de secondes

Une fois la connexion établie

L’écran affiche le temps disponible pour l'enregistrement d'une vidéo sur la carte SD.


L'état de charge de la batterie.

- Cliquer sur le cercle en bas pour lancer l'enregistrement de la vidéo.
- Vérifier que le temps s'écoule sur l'afficheur avant de la caméra.

## Visualiser les réglages de la caméra


Aide Mémoire GoPro Page 3/3

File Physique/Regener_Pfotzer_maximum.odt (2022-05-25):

# Le Regener-Pfotzer Maximum

Dans les années 1930, le physicien allemand Erich Regener (1881-1955) a réalisé d'importants travaux sur la mesure du taux de production d'ionisation en profondeur sous l'eau et dans l'atmosphère. Avec l'un de ses élèves, Georg Pfotzer, il découvre l'altitude à laquelle la production d'ionisation dans l'atmosphère atteint un maximum, appelé le maximum de Regener Pfotzer. Regener a été l'un des premiers à estimer la densité d'énergie des rayons cosmiques.

Lors du vol, le ballon traverse quelque chose appelé le Regener-Pfotzer Maximum, une couche de rayonnement maximal à environ 20 km au-dessus de la surface de la Terre. Ce graphique de rayonnement en fonction du temps pris lors d'un vol en ballon en juillet 2015 illustre le pic :


Quel est ce pic ? Pour le comprendre, commençons par l'espace lointain. Les rayons cosmiques sont essentiellement des débris subatomiques d'étoiles mourantes, accélérés à une vitesse proche de la lumière par des explosions de supernova. Ils voyagent à travers l'espace et s'approchent de la Terre dans toutes les directions, parsemant notre planète 24h/24 et 7j/7.

Lorsque les rayons cosmiques s'écrasent dans l'atmosphère terrestre, ils produisent un jet de particules secondaires et de photons qui est le plus intense à l'entrée de la stratosphère. Les physiciens Eric Regener et Georg Pfotzer ont découvert le maximum en utilisant des ballons dans les années 1930 et c'est ce que nous allons mesurer aujourd'hui.

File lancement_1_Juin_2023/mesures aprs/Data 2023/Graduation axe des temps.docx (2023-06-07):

| Projet Ballon Expérimental : Traitement des données | Sciences de l’Ingénieur Création et Innovation Technologique

Pour toutes les courbes l’échelle des temps sera graduée tous les 30 minutes.

Utiliser le format de l’axe horizontal suivant :


Rappel des couches de l’atmosphère :


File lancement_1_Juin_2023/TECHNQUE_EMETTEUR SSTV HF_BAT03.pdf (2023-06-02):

## Technique


## Radio-REF | 37

# Émetteur SSTV HF

Radio-club F4KMN, Le Mans
Matys Brule, Abdelkader Laklach, Nicolas Von Aesch


L’émetteur SSTV


### 1 Introduction

Nous sommes trois étudiants en BTS Informatique et Réseaux au lycée Touchard Washington du Mans. Dans le cadre de notre projet de fin d’année, nous programmons un émetteur SSTV HF afin d’envoyer des images. Cette carte sera embarquée dans le prochain vol du ballon sonde le 1er juin 2023 (1). La caméra de l’émetteur orientée vers le haut enverra régulièrement la progression du grossissement de l’enveloppe du ballon avant éclatement.
Cela nous permettra de vérifier la loi des gaz parfaits : PV = nRT.

### 2 La chaîne de transmission et de réception

L’image capturée par une ESP32CAM est convertie logiciellement dans le domaine fréquentiel puis envoyée vers un DDS programmable AD9850. Après amplification et filtrage, le signal SSB USB rayonne dans une antenne dipôle.
L’image SSTV encodée au format Scottie est reçue par un YAESU FT897-D ou avec un simple récepteur RTL-SDR. Une fois l’image reconstituée par QSSTV, elle sera enregistrée sur un serveur physique puis récupérée grâce à un script PHP et disponible pour les utilisateurs sur un site Web.

Synoptique de l’émetteur SSTV

La chaine de réception au sol
Nous mesurons l’évolution de la largeur de l’enveloppe du ballon en fonction de l’altitude de celui-ci toutes les 10 minutes. Pour cela nous prenons comme référence sur l’image la largeur du réflecteur radar (1 mètre). Il suffit d’utiliser le théorème de Thalès pour connaître le diamètre du ballon et ainsi en déduire le volume occupé par l’hélium.
Nous utiliserons les deux protocoles SSTV classiques, Martin ou Scottie. La fréquence de transmission sera effectuée sur la bande des 20 m avec une puissance de 0,5 W maximum.

### 3 Le protocole SSTV

Rappel : Le protocole SSTV (Slow Scan Television) est un protocole de transmission d’images analogiques en temps réel via des signaux radio. Il est utilisé par les radioamateurs pour transmettre des images de faible résolution entre eux. Le principe de base du SSTV est de convertir une image en une série de signaux audio qui peuvent être transmis via un émetteur classique. Ces signaux sont ensuite reçus puis décodés. Il existe plusieurs modes de transmission SSTV, chacun ayant des caractéristiques différentes en termes de qualité d’image et de rapidité de transmission. Les modes les plus utilisés sont Martin, Scottie et Robot.
Dans notre cas, le mode Scottie (QVGA) sera utilisé car c’est celui qui nous permet d’encoder une image en RGB (Rouge, Vert, Bleu) bien plus facilement que d’utiliser l’YUV.

Technique | N°976 | Juin 2023


## 38 | Radio-REF

Une option d’incrustation de texte permet de superposer à l’image un indicatif ou tout autre message utile à la transmission.

Un exemple de transmission d’image en QVGA Scottie 1

### 4 l’ESP32CAM

La caméra ESP32CAM et son support de programmation

L’utilisation de l’ESP32CAM présente plusieurs avantages pour un projet de ballon sonde. Tout d’abord, il s’agit d’un module compact et peu coûteux, ce qui permet de réduire considérablement le prix de l’émetteur.
De plus, l’ESP32CAM dispose d’une caméra OV2640 haute résolution interchangeable, ce qui permet d’avoir des images de qualité supérieure et de les sauvegarder sur une carte micro SD. En utilisant un simple DDS AD9850, l’émetteur ne comporte que très peu de composants pour transmettre des images claires et nettes à partir du ballon sonde, mais de définition plus faible.


Les caméras interchangeables OV2640
Avant d’utiliser la caméra en SSTV, il est vivement conseillé de se familiariser avec le module
en testant l’application démo « web server ».
En effet cette application permet de prendre connaissance de tous les réglages possibles de la caméra.
Quant à la programmation du module, celui-ci possède des documentations et des ressources présentant chacun des paramètres de la caméra (2).

Cependant, il est possible d’utiliser le format vidéo YUV pour transmettre des images avec le protocole Robot36 ou PD120 pour une image de plus grande définition (VGA).

Les différents modes de transmissions possibles avec l’émetteur


Les réglages de la caméra OV2640
En résumé, l’utilisation de l’ESP32CAM offre une solution compacte, peu coûteuse, facilement programmable avec un ESP32 et capable de capturer des images de haute qualité, ce qui en fait un choix idéal pour notre projet.

### 5 Le circuit intégré AD9850

L’AD9850 est un circuit intégré produit par Analog Devices permettant de générer des signaux sinusoïdaux et carrés jusqu’à 40 MHz, donc sur toute la bande HF.
L’utilisation de l’AD9850 dans notre projet a permis de produire des fréquences précises et stables nécessaires à la bonne transmission des signaux SSTV. Il n’était pas possible de prendre le DDS SI5351 car le temps de transfert sur le bus I²C est bien plus lent qu’avec la liaison SPI de l’AD9850.
L’AD9850 est utilisé dans les projets de communication radio, il existe donc plusieurs documentations et vidéos d’exemples et explicatives. De plus, c’est un circuit intégré que l’on retrouve souvent dans les revues radioamateurs.


Exemple de mire QVGA

### 6 Le schéma de l’émetteur

Le schéma structurel s’articule autour de
l’ESP32 (3). Un module série USB/TTL permet
de programmer le microcontrôleur. Il faudra cependant presser les deux boutons boot (GPIO0) et raz (RESET), puis relâcher le bouton raz pour pouvoir programmer.
Un buffer 74LS244 ou HCT permet d’adapter le niveau de tension 3,3 V vers le 5 V pour la liaison SPI de d’AD9850. À noter que la liaison SPI est partagée avec la caméra.
À l’origine, le prototype utilisait de simples transistors MOS en tant qu’adaptateur de niveau, mais il se produisait un conflit à la mise sous tension et la caméra ne pouvait pas s’initialiser. Le 74LS244 a résolu le problème.
Il ne reste plus que l’amplificateur de puissance classe E réalisé autour d’un RD16HHF1 ou de deux BS170 en parallèle. Il est possible de remplacer ce montage par un module amplificateur prêt à l’emploi.


Le schéma structurel de l’émetteur

# LA BOUTIQUE EN LIGNE

Vous pouvez, via le site du REF, vous connecter à la boutique en ligne, consulter, choisir et commander, puis procéder à un paiement sécurisé avec votre carte bancaire. N’hésitez pas, c’est pratique, c’est facile et il y a du choix. Votre commande enregistrée, le service Fournitures
du REF mettra tout en œuvre pour que vous receviez vos articles dans les meilleurs délais.

Il ne faudra pas oublier le filtre à adapter en fonction de la bande d’émission désirée.
Le gain de l’amplificateur peut également être réglé par l’ESP32CAM. Cependant, il faudra
« récupérer » un GPIO en plus sous l’ESP32,
avec un fil supplémentaire.
Ce contrôle de gain est réalisé avec un PWM suivi d’un filtre passe-bas afin de délivrer une tension continue réglable sur la grille du transistor MOS.


Le GPIO pour le contrôle de gain à récupérer sur l’ESP32CAM

### 7 Le logiciel

La programmation a été réalisée avec l’IDE Visual Studio Code et les extensions PlatformIO pour l’ESP32CAM. La page Web utilise
du code JavaScript et PHP ; elle dialogue automatiquement avec la base de données et sert d’interface pour afficher sur la page Web les photos prises.
Dans le programme fourni, vous trouverez un menu permettant de choisir l’action à réaliser, comme par exemple :
- sauvegarder une image sur la carte mSD ;
- choisir le mode SSTV ;
- envoyer une image SSTV ;
- envoyer une mire SSTV ;
- envoyer une image SSTV pré-enregistrée.


Menu de test accessible via le moniteur série Conclusion
Le projet de ballon sonde SSTV utilisant l’ESP32CAM et le DDS9850 a été une expérience incroyablement enrichissante pour nous, étudiants de BTS informatique et Réseaux.
Ce projet nous a permis de mettre en pratique les connaissances acquises tout au long de notre formation, ainsi que de développer de nouvelles compétences en matière de programmation et de développement électronique.
Nous sommes fiers de présenter le fruit de notre travail : un système capable de capturer et de transmettre des images de bonne qualité depuis un ballon sonde (4) jusqu’ à un récepteur au sol, en utilisant la technologie SSTV.
Nous espérons que ce projet pourra inspirer d’autres étudiants et développeurs pour explorer les possibilités offertes par l’ESP32CAM et le DDS9850.
Nous remercions M. Le Cren (F4GOH), M. Simier (F4JRE), M. Martin, M. Cruchet, M. Bernard (professeurs au lycée Touchard) de l’aide apportée tout au long de ce projet et de notre formation.


Les étudiants dans la salle informatique

73 et bonnes transmissions en SSTV.
(1) : https://vimeo.com/721096310
(2) : http://urls.r-e-f.org/gk721sd
(3) : https://github.com/f4goh/sstv
(4) : http://urls.r-e-f.org/om446db

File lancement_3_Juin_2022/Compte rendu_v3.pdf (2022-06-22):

## Ballon stratosphérique Lycée Touchard Washington


Desaunay Valentin, Neveu Benjamin, Suard Mickael , Maillard Clement, Porcheron Enzo

Professeurs référents : Bernard Didier, Le Cren Anthony, Simier Philippe

Compte rendu d'expériences Lancement du 3 juin 2022 | Lycée Touchard le Mans | page 1/19

## Table des matières

Compte rendu d'expériences Lancement du 3 juin 2022 | Lycée Touchard le Mans | page 2/19

## Bilan des mesures Ballon 2022

### 1 Présentation générale

Le projet de ballon stratosphérique, fut réalisé par 5 étudiants dans le cadre du projet de deuxième année du BTS Système numérique option informatique, durant l'année scolaire 2021-2022. Les idées motivant sa réalisation étaient la mesure de la radioactivité en altitude et l'utilisation d'un capteur GNSS pour suivre la position du ballon, et donc le récupérer. Le ballon a été lancée le 3 juin 2022 depuis Le Mans (72), suivi par une voiture et retrouvé quelques minutes après son atterrissage. Malgré quelques petits problèmes, les résultats des expériences ont pu être exploités avec intérêt.

### 2 Pesée - Vitesse de montée


Le ballon s’élève dans l’atmosphère grâce à la poussée d’Archimède.
Masse de la nacelle : 1455 g.

Nous sommes en dessous des 1800 g exigé par le cahier des charge. Le gonflage du ballon a été adapté (5,1 m³ d’hélium) afin d’avoir la portance qui permette une vitesse ascensionnelle de 5 m/s.

Vitesse ascensionnelle décollage = 4,74 m/s
Vitesse ascensionnelle à 4000 m = | 5,21 m/s
Vitesse ascensionnelle à 20000 m = | 5,41 m/s
Vitesse ascensionnelle à 30000 m = | 6,57 m/s
Compte rendu d'expériences Lancement du 3 juin 2022 | Lycée Touchard le Mans | page 3/19

### 3 Altitude d’éclatement

Plus il monte, plus la pression de l’air autour de lui, diminue. L’hélium occupe alors de plus en plus de volume : le ballon se dilate et finit par éclater.


Le centre de gravité étant situé dans la partie supérieure de la nacelle (coté opposé à la caméra), à l'éclatement du ballon, elle bascule sur le côté permettant ainsi à la caméra de filmer ce qui reste de l'enveloppe du ballon. Altitude à l’éclatement = 34 295 m
Les années précédentes la nacelle était plus lourde (1800g) le ballon était donc gonflé avec un volume d’hélium plus important et éclatait vers 30 000m. Conclusion , un ballon contenant moins d'hélium éclate à une altitude plus élevée.


Compte rendu d'expériences Lancement du 3 juin 2022 | Lycée Touchard le Mans | page 4/19


A ce moment, la chaîne de vol redescend vers la terre. Le parachute inséré initialement « en sapin » entre l’enveloppe du ballon et le réflecteur radar, joue alors son rôle de frein.

On remarque une vitesse de montée presque constante, entre 5 m/s et 6 m/s, et une vitesse de descente qui suit bien celle de la masse volumique de l'air.

Compte rendu d'expériences Lancement du 3 juin 2022 | Lycée Touchard le Mans | page 5/19

Montée

Descente

### 4 Alimentations

L'alimentation de la charge utile du ballon est une des parties essentielles pour le succès du projet. Elle est loin d’être évidente à concevoir et peut mener à l’échec total du projet. La conception doit prendre en compte plusieurs contraintes :

- La masse limitée de la charge utile, ce qui oblige à limiter le nombre d’accumulateur et à surveiller leur taux de charge.
- Le courant de pointe, alimenter de électronique d'instrumentation et un émetteur à partir de la même source n'est pas évident.
- Les conditions de température, les caractéristiques des accus n’étant pas trop documentées à
température ambiante, elles sont inconnues aux très basses températures.

Bilan électrique
Les cartes doivent être alimentées avec une
- Tension d’alimentation 5V
- | Consommation | 170 mA (250mA avec l’émetteur du WIFI).

Réalisation


| | Trois accumulateurs 18650 (lithium ion) de capacité 3000 mAh sont utilisées. Leur tension nominale est 3,6 V. Ils sont montés en série. La tension au bornes de l’ensemble atteint 12,6 V lorsqu’ils sont complètement chargés et 9,6 V lorsqu’ils sont déchargés. Le travail de surveillance est effectué grâce à une carte électronique de gestion appelée BMS “Battery Management System”. Le BMS interrompt la décharge des cellules avant que cela ne devienne critique pour leur durée de vie.

Il interrompt aussi la charge des cellules avant qu’elles ne soient trop chargées Il optimise un chargement homogène d’une cellule à l’autre
Il vérifie la température des cellules.


un convertisseur DC DC buck, (hacheur série) abaisse la tension à 5v. Le capteur INA219 est aussi utilisé pour mesurée le courant et la tension. Il est donc possible de connaître en temps réel l’état de charge des accumulateurs grâce au calcul du SOC “State Of Charge” en %

En définitive une carte spécifique a été développée pour connecter l’ensemble des éléments.

Avant le lancement la charge des batteries est maintenue à l’aide d’une alimentation nourrice extérieure à la nacelle. Juste avant le lancement la nourrice est déconnectée. la tension au décollage était de 12,6 V à la fin du vol 12V, la charge restante était de 2393 mAh soit un taux de charge de 79 %.

L’alimentation à parfaitement remplit sa fonction.

Compte rendu d'expériences Lancement du 3 juin 2022 | Lycée Touchard le Mans | page 6/19

### 5 Fréquences et Indicatifs des émetteurs

La nacelle est équipée de trois émetteurs radios:
- APRS sur LoRa fréquence 433,775 MHz indicatif F4KMN-11
- APRS sur FX25 fréquence 137,05 MHz indicatif F4KMN-13
- Sigfox fréquence 868 MHz indicatif C50EE9

Les émissions sont décalées
- trame APR FX25 à la seconde 57
- trame APRS Lora à la seconde 20
- trame Sigfox à la seconde 40 Indicatif de la voiture suiveuse F4KMN-10


La voiture suiveuse est arrivée sur la zone prévisionnelle atterrissage.

Compte rendu d'expériences Lancement du 3 juin 2022 | Lycée Touchard le Mans | page 7/19

### 6 Le suivi de la trajectoire

Le taux de mise à jour pour le suivi est d'une fois par minute sur la fréquence 433 MHz (Lora) et d’une fois toutes les deux minutes pour les fréquences 137,05 MHz (APRS FX25) et 868 MHz (Sigfox).


Temps de vol

Départ 13h 44' 15'' | Arrivée | 16h 29' 55'' | durée | 2h 45' 40''

Sur la carte TTGO « LoRa », la puce GNSS a cessé de fonctionner à une altitude d'environ 12 000
m. Les positions du ballon au-dessus de 12 000 m était donc totalement fausse. Cependant le fonctionnement est revenu à la normale à la descente. On remarque que les points sont plus serrés que sur la trajectoire précédente car le taux de mise à jour est de une toute les minutes.
Compte rendu d'expériences Lancement du 3 juin 2022 | Lycée Touchard le Mans | page 8/19


Après quelques recherches sur le WEB, nous découvrons que la puce GNSS (NEO-6M) est configurée par défaut sur le modèle de plate-forme dynamique Portable (altitude max 12000m). Toutefois elle peut enregistrer les rapports d'altitude et de positionnement jusqu'à 160 000 FT (48 768 m), nous devons nous assurer d'activer le modèle de plate-forme dynamique (voir tableau ci-dessous) pour ajuster le moteur de navigation à l'environnement d'application attendu. le modèle Airborne1g est prévu pour fonctionner jusqu'à 50 km d'altitude.

Compte rendu d'expériences Lancement du 3 juin 2022 | Lycée Touchard le Mans | page 9/19


Vitesse mesurée de descente après éclatement

13941 pieds = 4249 m 4249 / 120 = | 35,40 m/s | 127 km/h

Le modèle Airborne <1g est prévu pour fonctionner jusqu'à une vitesse verticale de 100m/s.

Conclusion
Le modèle Airborne <1g est le mieux adapté.
Par contre quand le ballon est retombé au sol, il serait bien de revenir au modèle Stationary qui donne la meilleur précision de position possible.

Extrait de programme pour adapter le modèle
myGPS.setDynamicModel(DYN_MODEL_AIRBORNE1g);
// Verification de la prise en compte
uint8_t newDynamicModel = myGPS.getDynamicModel();
if (newDynamicModel == 255)
{
Serial.println(F("***!!! Warning: getDynamicModel failed !!!***")); }
else
{
Serial.print(F("The new dynamic model is: ")); Serial.println(newDynamicModel);
}
Compte rendu d'expériences Lancement du 3 juin 2022 | Lycée Touchard le Mans | page 10/19

### 7 La mesure des radiations

L'expérience principale consiste à mesurer la radioactivité en altitude, ce qui présente plusieurs difficultés. Divers capteurs sont possibles, mais les contraintes de masses et de coût limitent énormément les possibilités. En définitive, nous avons fait au plus simple, en choisissant un compteur Geiger du commerce, ce qui permet de mesurer le flux de particules d'une certaine énergie dans l'élément sensible. Le compteur, choisi pour son coût, sa simplicité et sa disponibilité, est un modèle radiation watch. (Plage de mesure de 0,05 uSv/h à 10 mSv/h entre 0,01 cpm et 300 Kcpm)


Le rayonnement est composé de photons gamma et de particules capables de provoquer, directement ou indirectement, la formation d'ions (par arrachement d'électrons) dans la matière qu’ils traversent.
La détection du rayonnement ionisant repose sur un type particulier de diode, la diode PIN. PIN pour Positive Intrisic Negative fait référence directement à la manière dont est constitué le composant. Dans une diode PIN on trouve entre les zones P et N une zone non dopée dite intrinsèque.
La structure PIN permet la détection de photons, un peu à la manière d'un tube Geiger-Muller avec un effet cascade et une brève conductivité. Cela signifie que si un rayon de haute énergie est absorbé, un signal détectable d'électrons est généré. l'absorption photoélectrique est dominante dans la région d'énergie gamma d'intérêt entre 5 keV et 100 keV. Les détecteurs basés sur l'absorption directe dans le silicium constituent une alternative peu coûteuse par rapport au détecteur à gaz (tube Geiger-Muller).

Notre expérience vise à confirmer les données concernant le maximum Regener-Pfotzer. Nous n'avons trouvé aucune étude européenne sur le maximum de Regener-Pfotzer lors de nos recherches.
Lors de nos mesures nous avons constaté un maximum à 69369 pieds = 21 143 m → 107 cpm La dose de rayonnement diminue comme prévu lorsque le capteur atteint des altitudes plus élevées que ce Maximum dit de Regener-Pfotzer .
Compte rendu d'expériences Lancement du 3 juin 2022 | Lycée Touchard le Mans | page 11/19


Conclusion : Nous observons bien un maximum pour l'altitude 20000m. La hausse due au rayonnement apparaît plus tardivement lors de la descente, car la vitesse de descente est plus importante que celle de la montée à ces altitudes.

Compte rendu d'expériences Lancement du 3 juin 2022 | Lycée Touchard le Mans | page 12/19

Regener-Pfotzer Maximum

Lancement

éclatement

ascension | descente

Cpm

temps

### 8 Evolution de la température avec l'altitude

La température extérieure est mesurée par un thermocouple de type K (Plage :-100°C à 500°C ). La difficulté dans l’utilisation du thermocouple est que la tension à mesurer est très faible, avec des variations d'environ 50 uV par °C avec une compensation de température froide. Pour toutes ces raisons, nous utilisons une puce d'interface MAX31855 qui fera le gros du travail, nous permettant d'intégrer facilement le capteur sans trop de difficulté.
La température minimale a été atteinte à 37355 pieds = 11 385 m → -45 °C

Altitude (m); Température °C; Troposphère; Tropopause; Stratosphère

Le gradient thermique dans la troposphère est : -5,9 °C/Km
Le gradient thermique dans la tropopause est : +0 °C/km
Le gradient thermique dans la stratosphère est : +2,22 °C/km

Conclusion les valeurs de température mesurée sont proches des valeurs de l'atmosphère standard dite «ISA» (International Standard Atmosphere)

Compte rendu d'expériences Lancement du 3 juin 2022 | Lycée Touchard le Mans | page 13/19

### 9 Température minimale à l’intérieur de la nacelle

Un capteur mesure la température à l'intérieur de la nacelle. L’objectif est d’avoir une température positive à l’intérieur de la nacelle pendant toutes les phases du vol.

Ainsi la nacelle a été entièrement recouverte d'une couverture de couleur or pour retenir la chaleur interne.
La couverture est revêtue de deux faces métallisées distinctes, respectivement dorée et argentée. Ces faces répondent à deux fonctions distinctes : le côté argenté, réfléchit 90% du rayonnement infrarouge, tandis que le côté doré absorbe 50% de la chaleur incidente. De ce fait, en positionnant la face dorée vers l'extérieur, la nacelle est protégée du froid, en retenant sa chaleur.


La température minimale, lors du vol, a été de +2,2 °C obtenue pendant la descente à 7000m d'altitude.

Eclatement; Montée; Descente

La nacelle s’est refroidie pendant la montée jusqu'à 22000m, puis elle s’est réchauffée. En descente, au environ de 7000m la température minimale est atteinte. Il y a donc eu un refroidissement continu de la nacelle par conduction thermique.
Les hausses de température observées dans les altitudes basses et hautes sont dues aux transferts de chaleur par rayonnement infra-rouge.
Compte rendu d'expériences Lancement du 3 juin 2022 | Lycée Touchard le Mans | page 14/19

### 10 Evolution de la pression avec l'altitude

Pression (hPa); Altitude (m)

La pression est réduite :
- d'un facteur 2 à l'altitude 5500 m (513 hPa)
- d'un facteur 10 à 16547m (100 hPa).
Ces mesures sont conformes au t (https://fr.wikipedia.org/wiki/Variation_de_la_pression_atmosph%C3%A9rique_avec_l'altitude) ableau de la pression atmosphérique nominale selon l'altitude, (https://fr.wikipedia.org/wiki/Variation_de_la_pression_atmosph%C3%A9rique_avec_l'altitude) dans la troposphère.
Compte rendu d'expériences Lancement du 3 juin 2022 | Lycée Touchard le Mans | page 15/19

### 11 Trames APRS via LoRA

Pendant le vol, une trame par minute est émise, soit au total 177 trames transmises. Les trames ont été entendues et relayées par les relais suivants.


Nombre de trames relayées par station (grep F1ZCK-10 Trame_F4KMN-11.txt | wc)
F1ZCK-10 | 324 | F4GXP-10 | 5
F4ECA-10 | 304 | ON5YW-15 | 4
F4KMN-1 | 163 | HB9TQJ-3 | 4
F4GOH-1 | 122 | ON3CRX-10 | 3
F4GXP-5 | 93 | ON7WP-11 | 2
F4HVU-10 | 72 | F4EWJ-10 | 2
F1ZIF-10 | 46 | DB0MOE-10 | 2
F8GHE-10 | 45 | ON7KY-12 | 2
DB0WTH-12 | 27 | ON8SV-15 | 2
DF7RW-2 | 19 | ON8BZ-13 | 1
DB0HRW-10 | 15 | ON7KY-11 | 1
F4DVK-10 | 14 | DB0NOR | 1
F5RVX-10 | 11 | DB0WK-10 | 1
ON4JPS-10 | 8 | ON3MPE-10 | 1
ON7TA-10 | 7 | F4GXP-3 | 1

Remarque : Les Relais F1ZCK-10 et F4ECA-10 ont bouclé sur eux-mêmes, ce qui explique qu’ils ont entendu plus de messages que le ballon en a envoyés.

Compte rendu d'expériences Lancement du 3 juin 2022 | Lycée Touchard le Mans | page 16/19

### 12 Atterrissage

Le véhicule suiveur à emprunté l’autoroute ; il est arrivé à proximité du point de chute prévisionnel environ 30 minutes avant l’atterrissage. Finalement, le véhicule suiveur est arrivé sur la zone du point du chute à 16h32 deux minutes après l’atterrissage (16h30). La poursuite du ballon a donc été un succès.
La charge utile avec le réflecteur et le parachute se sont posé sur une petite route de campagne.

route de l’épine Jousset
commune de Tourouvre au Perche dans l’Orne
Latitude : 48,562312° | Longitude: 0,684471° | heure 16h 29' 55''


Son état général est très bon, les cartes n’ont pas bougé, seule les fixations de la carte TTGO ont cédés à l’impact.

L'énergie du choc correspond à l'énergie cinétique de la nacelle.

V = 2,98 ms⁻¹ masse = 1,455 Kg

E=

1
2

m v

2=

1
2

∗1,455∗2,98=6,46J

Compte rendu d'expériences Lancement du 3 juin 2022 | Lycée Touchard le Mans | page 17/19


Il faudra modifier la fixation de cette carte afin d’avoir 4 points de fixation! Il faudra prévoir de renforcer les pieds de la nacelle.

### 13 Source des logiciels sur Github

Les programmes informatiques sont disponibles sur les dépôts Github des étudiants et des professeurs.
Logiciel serveur web Valentin Desaunay (https://github.com/ValentinDesaunay/Projet_Ballon_2022)
Logiciel carte Sigfox Benjamin (https://github.com/BenjaminNeveu/Ballon_sonde) Neveu (https://github.com/BenjaminNeveu/Ballon_sonde)
Logiciel carte APRS Lora & iGate Anthony Le Cren (https://github.com/f4goh/lora-aprs-esp32) Logiciel carte APRS FX25 Philippe Simier (https://github.com/PhilippeSimier/Ballon_stratospherique_aprs_2022)
Compte rendu d'expériences Lancement du 3 juin 2022 | Lycée Touchard le Mans | page 18/19

### 14 Conclusions générales

Pour conclure, nous pouvons maintenant répondre aux questions que nous nous sommes posées au début de notre projet. Le flux de rayonnement augmente-t-il réellement en altitude et, si tel est le cas, la différence de niveaux de rayonnement est-elle suffisamment importante pour constituer une menace pour les humains ?
Nous avons pu constater qu'il y a une augmentation constante du rayonnement à mesure que l'altitude augmente en raison de l'effet de protection de l'atmosphère, jusqu'à une hauteur d'environ 20 km où le rayonnement cosmique secondaire est le plus intense en raison de la formation des cascades de particules.
Le ballon a occupé une place importante pour nous tous et durant toute une année. L'organisation de projet, les connaissances théoriques acquises, les difficultés levées et le savoir-faire développé marquent déjà le projet d'une très grande réussite.
Après de nombreuses péripéties le jour du départ du fait de la météo orageuse, le ballon a pu prendre son envol. Malgré quelques difficultés les résultats obtenus sont intéressants et en tout cas confirment le succès technique du projet.
Compte rendu d'expériences Lancement du 3 juin 2022 | Lycée Touchard le Mans | page 19/19

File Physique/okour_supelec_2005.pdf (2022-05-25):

# Ballon Okour


# Supélec Espace 2003-2004

# Claire Cizaire Nicolas Couronneau Aline Meuris Benoît Legrand

1/63 | 28/09/05

# Sommaire

Supélec Espace
Supélec - Plateau du Moulon - 91192 Gif-sur-Yvette Cedex espace@supelec.fr
Association déclarée à la préfecture de l’Essonne – n°310242

## 1. Présentation générale

Le projet de ballon stratosphérique Okour de Supélec Espace, association de l'école Supélec (campus de Gif sur Yvette en Essonne), fut réalisé par 4 étudiants durant l'année 2003-2004. Les idées motivant sa réalisation étaient l'utilisation d'un GPS pour suivre le ballon, et donc le récupérer, et la mesure de la radioactivité en altitude.
Commencé en octobre, le projet a été réalisé au sein de l'association, en dehors de la scolarité, et avec des moyens techniques et financiers assez limités. Pour pallier au manque de matériel, nous avons largement utilisé la base technique de l'association nationale Planète Sciences.
Après un premier report, le ballon fut finalement lâché le 19 septembre 2004 depuis Buthiers (77), suivi par deux voitures et retrouvé quelques minutes après son atterrissage. Malgré quelques problèmes avec la réception des télémesures, les résultats des expériences ont pu être exploités avec intérêt.
Ce projet a été doublement couronné de succès, car en plus de la réussite du vol, il fut sélectionné par l'ESA pour le programme étudiant du 24ème Congrès International d'Astronautique (IAC 2004). L'un d'entre nous a ainsi pu partir présenter le projet à Vancouver (Canada), en octobre.

## 2. Expériences embarquées

## 2.1. Synoptique

PIC 16F876; Modulateur FSK GPO; USART; Carte environnement; T° intérieure; T° extérieure; Pression; GSM; GPS; Emetteur; Compteur Geiger

## 2.2. Mesure de radioactivité

### 2.2.1. Présentation

L'expérience principale consiste à mesurer la radioactivité en altitude, ce qui présente plusieurs difficultés :

– Il est très difficile de trouver des prédictions pour les altitudes des ballons. En dessous de 10km, on peut trouver des études concernant l'exposition aux rayonnements des personnels navigants, et au dessus de 300km on peut trouver des résultats d'expériences embarquées à bord de satellites.

– Dans les quelques documents présentants des résultats à nos altitudes, les grandeurs étudiées ne sont pas mesurables dans un ballon, en raison de l'équipement nécessaire. On trouve des mesures d'intensité du rayonnement en fonction de son énergie, du flux de certaines particules données, etc. Les différentes énergies des particules compliquent l'estimation du débit de dose qui serait donné par un compteur Geiger classique.

– Divers capteurs sont possibles, mais les contraintes de masses et de coût limitent énormément les possibilités. Après quelques échanges intéressants avec l'IRSN (Institut de Recherche en Sûreté Nucléaire), il s'est avéré que la mesure la plus intéressante est le LET : Transfert d'Energie Linéique, qui permet de mesurer l'énergie des rayonnements. Cependant, ces capteurs sont assez coûteux et le traitement du signal qui doit suivre est assez complexe (échantillonnage de l'impulsion de la particule pour en mesurer l'énergie).
En définitive, nous avons fait au plus simple en choisissant un compteur Geiger du commerce, ce qui permet de mesurer le flux de particules d'une certaine énergie dans le tube. Le compteur, choisi pour son coût, sa simplicité et sa disponibilité, est un modèle Quartex RD8901.

### 2.2.2. Modification du compteur

On souhaite récupérer les impulsions en sortie du tube, ce qui demande d'étudier un peu le fonctionnement du compteur. A l'oscilloscope, on observe que les impulsions en sortie du tube se présentent comme des pics d'environ 50 ns, et de tension maximale 300V. La mesure de tensions n'a ici pas beaucoup de signification, car les charges transférées sont extrêmement faibles, et le courant maximal est certainement de quelques nanoampères. Le fabricant relie ce signal à l'entrée d'une bascule RS par l'intermédiaire d'une résistance de 1MOhm. Lorsque qu'une particule traverse le tube, l'impulsion met à 1 la sortie de la bascule reliée à l'entrée du microcontrôleur du compteur (un Atmel). Le microcontrôleur acquitte alors la nouvelle impulsion en remettant à zéro la sortie de la bascule (mécanisme d'interruption externe). On utilisera un montage similaire, en récupérant le signal en sortie du tube et en l'injectant sur une entrée d'interruption du microcontrôleur PIC. Entre les deux, on placera toutefois une porte en logique rapide et CMOS (la commutation doit se faire avec un courant quasi-nul, seules quelques charges sont transférées en sortie du tube), qui fera office de « fusible » pour protéger l'entrée du PIC. Ce montage n'est pas très propre mais fonctionne très bien, avec le composant (74hc85) pistocollé sur le circuit d'origine.


Illustration 1: Vue du compteur Geiger démonté


### 2.2.3. Calibration du compteur

Nous avons eu accès à un compteur professionnel de référence et à deux sources radioactives d'énergies différentes : Cobalt 60 et Sodium 22. L'objectif était de trouver la relation entre le nombre d'impulsions et le débit de dose mesuré.
D'après la notice du Quartex RD8901, la gamme des énergies mesurables est de :
- 100 keV à 1,2 MeV pour les particules beta
- 350 keV à 1,2 MeV pour les gamma
Sensibilité du tube : 78 impulsions / µRem (donc : 78 cps = 1 µRem / s = 3600 µRem /h = 36 µSv / h soit 0,46 (µSv/h) / cps)
2.2.3.1. Déroulement

On place la source à égale distance des deux compteurs. Comme le rayonnement est isotrope, les deux compteurs doivent recevoir la même dose. On intègre les mesures sur 3 minutes pour le Quartex (en modifiant le programme de vol pour compter 3 minutes d'impulsions), le Radiagem intégrant sur quelques dizaines de secondes (mais on ne note aucune fluctuation sur le radiagem).
On renouvelle 3 fois chaque mesure avant de passer à une autre distance.
2.2.3.2. Calibration Cobalt 60 (Gamma à 1,1 et 1,3 MeV)

Illustration 2: Vue du compteur Geiger démonté

Illustration 3: Relevés bruts calibration Cobalt 60

Distance (cm) | 10 | 7 | 5 | 4 | 3 | 2
Mesure Gamma (µSv/h) | 1,90 | 3,70 | 6,30 | 6,90 | 10,60 | 15,50
Moyenne (cps) | 2,67 | 7,65 | 12,54 | 14,47 | 20,64 | 30,17
Variance | 20,23 | 50,82 | 84,56 | 74,29 | 102,99 | 158,56
Ecart type | 4,50 | 7,13 | 9,20 | 8,62 | 10,15 | 12,59

Calibration using Cobalt 60; Dose rate (µSv/h), as read on Radiagem; Count per second (cps)

Calibration Sodium 22 (beta à 550 keV et gamma à 1,2MeV)

Illustration 4: Graphe relevés bruts calibration Cobalt 60

Illustration 5: Relevés bruts calibrations Sodium 22

Distance (cm) | 10,5 | 7 | 5 | 4 | 3 | 2 | 1
Mesure Gamme (µSv/h) | 1,3 | 3,1 | 6,5 | 6,9 | 10,3 | 16,3 | 32
Moyenne | 2,18 | 4,21 | 8,09 | 11,56 | 14,48 | 28,42 | 88,49
Variance | 14,33 | 28,23 | 25,43 | 51,66 | 83,77 | 109,22 | 342,88
Ecart type | 3,79 | 5,31 | 5,04 | 7,19 | 9,15 | 10,45 | 18,52

A l'issue de la calibration, on note une correspondance linéaire entre le Radiagem (compte de référence) et le Quartex RD8901 embarqué dans le ballon, pour une mesure de particules gamma.
La calibration avec la source Sodium semble montrer une forte sensibilité aux radiations de basses énergies à débit élevé, par rapport à des particules d'énergie plus élevées même de même flux.
Régressions linéaires :
- Cobalt 60 : (0,5 x (cps) + 0,07) (µSv/h)
- Sodium 22 : (0,34 x (cps) + 3,29) (µSv/h)
Au final, on prendra la relation annoncée dans la notice qui se trouve être bien vérifiée avec une marge de 10 % sur la calibration au Cobalt.

Illustration 6: Graphe relevés bruts calibration Sodium 22 (µSv/h – cm)

1,3 | 3,1 | 6,5 | 6,9 | 10,3 | 16,3 | 32

0,00

10,00

20,00

30,00

40,00

50,00

60,00

70,00

80,00

90,00

## 2.3. Mesures de température et pression

Nous avions choisi de réaliser une carte analogique regroupant des mesures de température à l’intérieur et à l’extérieur de la nacelle, ainsi qu’une mesure de pression. Face aux difficultés lourdes rencontrées au moment des tests de télémesure, nous avons opté en dernier recours pour la programmation de deux capteurs numériques de température et nous avons supprimé la mesure de pression.

### 2.3.1. Prédéterminations

- Température atmosphérique de 0 à 40 000 m comprise entre –60°C et 35°C
- Température à l’intérieur de la nacelle comprise entre –10°C et 30°C.
- Pression atmosphérique de 0 à 40 000 m comprise entre 5 kPa et 101 kPa
- Tensions de sortie comprises entre 0 et 5V.

### 2.3.2. Carte analogique

Le capteur analogique de température utilisé est le AD590, qui délivre un courant dont la valeur en µA correspond à la température en Kelvin. Des simulations sur P-Spice ont permis d’établir la valeur des résistances de gain et d’offset pour sortir une tension entre 0 et 5V. Un étalonnage a été réalisé dans l'étuve de la base technique de Ris-Orangis (pouvant fournir des températures de –80°C à 80°C) pour régler avec précision les résistances ajustables.

2.3.2.1. Schéma de la carte analogique

(en annexe)

Illustration 7: Cartes électroniques en étuve, sans le ballon

2.3.2.2. Résultats de l’étalonnage

Température extérieure; Température (°C); ortie (V; Sortie temp. 1; Droite -0,059x+1,153; Température intérieure; rtie (V)

Sortie temp. 2 et 3 | Droite -0,981x+2,825
2.3.2.3. Problèmes de CEM

Une chaîne de télémesure complète a été mise en œuvre pour observer les résultats reçus au sol. Le fonctionnement de l’émetteur à proximité de la carte analogique perturbait totalement les mesures de température. On observait des fluctuations de l’ordre du volt, des saturations subites des capteurs… Nous avons isolé au maximum la carte de l’émetteur (boîte d’aluminium, éloignement des capteurs, blindage des câbles, plan de masse…) pour limiter les courants parasites. Face au manque de fiabilité des résultats, nous avons remplacé toute cette carte par des capteurs numériques.

### 2.3.3. Programmation de capteurs numériques

Nous avons embarqué deux capteurs TMP100, un pour mesurer la température intérieure, un pour latempérature extérieure.
* | Driver pour le capteur de température TMP100

#ifndef __TMP100_C__

#define __TMP100_C__

#include "ledvie.c"

/**
| * Retourne la température lue par le capteur <code>n</code>
*
| * @param numéro du capteur (<b>pas</b> adresse I2C). * @return température en degrés, signed int16

*/
int16
lireTmp100 (int8 n)
{
| int16 val; int k = 0;
| restart_wdt (); // Start conversion (W) // configuration du capteur i2c_start (); // adresse + test if(i2c_write (0x90 | (n << 1))) { // Problème I2C : esclave inaccessible for (k = 0; k < 10; k++) { delay_ms (200); changerLed (); } } // pointeur sur registre de configuration i2c_write (0x01); // registre de configuration i2c_write (0); i2c_stop ();
| //lecture de la température i2c_start (); // adresse i2c_write (0x90 | (n << 1)); // pointeur sur registre de température i2c_write (0);
| i2c_start (); i2c_write (0x90 | (n << 1) | 1);
| val = (i2c_read () << 8); val += i2c_read (0); i2c_stop ();
| return val;
}

#endif // __TMP100_C__

## 2.4. Localisation GPS

### 2.4.1. Présentation

On utilise un récepteur Motorola Oncore VP, à 8 canaux parallèles, qui s'interface simplement avec une liaison série, au format RS232 et aux niveaux TTL. Ce modèle est disponible à petit prix comme fin de stock.

L'alimentation se fait sous 5V et 250mA, avec l'antenne amplifiée. Cette consommation est assez importante, surtout pour un ballon. Les nouveaux récepteurs (M12, Laipac), fonctionnent en 3,3V et consomment beaucoup moins. Ils sont très intéressants pour des ballons.


### 2.4.2. Position de l'antenne GPS

Pour faire taire certaines craintes, nous n'avons rencontré aucun problème d'interférence entre l'émetteur Kiwi et le GPS. L'antenne (modèle patch amplifié) est fixée à même le ballon, avec une plaque de cuivre comme plan de masse.

Illustration 8: Motorola Oncore VP

Illustration 9: Plan de travail pour le développement de l'interface GSM-GPS (à la base technique de Ris-Orangis)


Les problèmes déjà rencontrés entre un module GPS et l'émetteur sont peut-être dus à des interférences couplage sur les alimentations, plutôt que par rayonnement sur les étages d'amplification du GPS. Ici nous utilisons deux blocs de piles distincts pour l'émetteur et pour le GPS. Nous n'avons rencontré aucun problème avec l'utilisation d'une alimentation à découpage (filtrée avec des filtres LC en pi et des ferrites) pour le GPS.

## 2.5. Expérience GSM

Note : Cette partie reprend une étude réalisée par le binôme Claire-Nicolas dans le cadre d'un projet scolaire de 1ère année.

### 2.5.1. Présentation

La liaison radio de la télémesure est souvent interrompue à proximité du sol, suite à la présence d’obstacles (forêt, immeubles) ou de dommages lors de l’atterrissage.
Comme nous ne souhaitons pas perdre le matériel embarqué, nous voulons connaître avec précision le point de chute du ballon. Nous utiliserons un téléphone GSM pour envoyer les dernières positions du ballon. On considère en effet que le réseau GSM est plus fiable que notre télémesure.
Notre projet consiste à récupérer les données de position du GPS, les envoyer par SMS à un portable au sol, via un autre portable embarqué dans le ballon. Le message devra être répété à intervalles réguliers sur le dernier kilomètre pour être sûr de la présence du réseau.

### 2.5.2. Cahier des charges

2.5.2.1. Fréquence d’envoi

L’envoi des SMS n’est prévu que durant la dernière partie de la descente. On peut aussi envisager l’envoi d’un SMS de bon fonctionnement lors de l’ascension. Il reste à définir le nombre d’envois et l’altitude à partir de laquelle on peut espérer une bonne réception. L’absence de documentation à ce sujet est problématique.
En utilisant les documentations des fabricants d’antennes, on a une idée du diagramme de rayonnement, très concentré dans un plan horizontal. De plus les opérateurs inclinent souvent les antennes (tilt) vers le bas pour améliorer les transmissions. Pour une ouverture de l’antenne de la station de base de 8° avec un tilt de 6°, l’atténuation est de –3db à 2° au dessus de l’horizon.

Illustration 10: Placement antenne GPS, sur le haut de la nacelle

On peut se fixer 5° pour la réception, et avec une portée optique de 30km (recommandation de portée de la norme GSM), l’altitude maximale de réception est :

H = 30.sin(5°)
H = 2,6km.

L’idéal serait d’obtenir une dizaine de messages jusqu’à l’atterrissage, donc un message tous les 250m.
La vitesse de descente du ballon, imposée par le parachute CNES, est de 5m/s. Il faudrait donc transmettre toutes les 50s.
A priori, on peut se permettre une fréquence d’envoi plus élevée, la durée d’un envoi étant de quelques secondes. Un message tous les 100m serait bien.
2.5.2.2. Contenu du message

Ce sont les données essentielles à la localisation, en provenance du GPS. Un seul message SMS ne peut dépasser 160 caractères.

dd°mm.mmmm (N/S) | ddd°mm.mmmm (W/E) aaaaaM | hh :mm :ss
altitude | longitude | altitude | heure

Taille : 40 caractères (espaces compris).

2.5.2.3. Alimentation

La batterie du mobile permet une veille d’au moins 24h et le vol est prévu pour durer 3h. Mais le mobile risque d’user inutilement la batterie en essayant de communiquer avec la station de base au cours du vol (un burst à pleine puissance au moins toutes les 6 min d’après la norme GSM). De plus le mobile qu’on nous prêtera sera probablement assez vieux et donc les performances de la batterie seront très dégradées.
Il est donc souhaitable d’avoir un moyen d’allumer et d’éteindre le portable.
On nous a conseillé d’allumer le mobile à des intervalles réguliers pour maintenir la batterie à sa température de fonctionnement (risque de non-rallumage si elle est trop froide).

2.5.2.4. Récupération des données GPS

L’architecture du ballon est centrée autour d’un bus I2C qui permet les communications entre les différentes expériences.
Une carte à base de microcontrôleur PIC 16F876 est consacrée à la gestion du module GPS et aux télémesures. Elle possède également une liaison I2C pour accéder aux convertisseurs A/N des diverses expériences. On utilisera cette liaison I2C pour transmettre les informations de position du message SMS.
La carte GPS est un périphérique I2C maître, la carte GSM est donc utilisée en périphérique esclave. Les adresses I2C 0x04→0x0A sont dédiées à des utilisations spéciales, on choisit 0x04 pour ce périphérique.
Les données venant du GPS seront transmises en ASCII, ce qui simplifie beaucoup leur utilisation dans un message texte SMS. De plus, en utilisant les trames NMEA du GPS, on travaille entièrement en mode texte, et on se passe donc de conversion flottant→texte très gourmandes en mémoire.
On transmettra donc, en ASCII :

Index
0 | Latitude | Degrés | 10
1 | | | 1
2 | | Minutes | 10
3 | | | 1
4 | | | 1/10
5 | | | 1/100
6 | | | 1/1000
7 | | | 1/10000
8 | | N/S (S ???) | ‘N’/’S’

## Carte GPS

## GPS embarqué

## Carte GSM

## GSM : Siemens C35

## GSM récepteur

Bus I2C | Autres cartes

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
Longitude | Degrés | 100
10
1
Minutes | 10
1
1/10
1/100
1/1000
1/10000
W/E | ‘W’/’E’
19
20
21
22
23
Altitude | Mètres | 10000
1000
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
Heure | Heures | 10
1
Minutes | 10
1
Secondes | 10
1
30 | Validité | 0 position non valide
1 position 2D valide
2 position 3D valide
2.5.2.5. Envoi du SMS
- Interface GSM - PIC
L’envoi d’un SMS nécessite une liaison avec le mobile GSM. L’interface la plus utilisée sur les anciens mobiles est une liaison série asynchrone. La documentation concernant les brochages des téléphones et les paramètres de connexion est très difficile à trouver, les fabricants ne communiquent guère sur ces sujets.
Les commandes pour contrôler le mobile sont héritées des modems Hayes des PCs : ce sont les commandes AT. La documentation des commandes AT supportées par les mobiles est très variable selon les fabricants. Elles sont globalement standardisées, mais peuvent différer pour les fonctions spéciales.
- Composition et envoi du SMS La commande AT permettant l’envoi d’un SMS est la suivante, sur toutes les documentations rencontrées
AT+CMGS


Siemens – AT Command Set Reference Manual

Pour envoyer les SMS, plusieurs modes sont à disposition. Entre autres le mode PDU – Protocol Data Unit – est le plus général et le mieux supporté. En contrepartie il est également plus difficile de l’utiliser, le format des messages PDU étant assez contraignant (alphabet 7-bits, héxa inversé). Ce mode fait l’objet de la recherche documentaire.

2.5.2.6. Mode PDU
- Champs du message
Champ | Description
TP-MTI | First octet
TP-MR | TP-Message-Reference
TP-DA | TP-Destination-Address
TP-PID | TP-Protocol-Identifier
TP-DCS | TP-Data-Coding-Scheme
TP-VP | TP-Validity-Period
TP-UDL | TP-User-Data-Length
TP-UD | TP-User-Data

On se restreint à l’étude des champs utilisés par la commande AT. Il existe d’autres champs (plus proche du réseau) que le téléphone GSM se charge de remplir.
Premier octet : TP-MTI
TP-MTI | TP-Message-Type-Indicator | 2b | Parameter describing the message type.
TP-RD | TP-Reject-Duplicates | b | Parameter indicating whether or not the SC shall accept an SMS-SUBMIT for an SM still held in the SC which has the same TP-MR and the same TP-DA as a previously submitted SM from the same OA
TP-VPF | TP-Validity-Period-Format | 2b | Parameter indicating whether or not the TP-VP field is present.
TP-RP | TP-Reply-Path | b | Parameter indicating the request for Reply Path.
TP-UDHI | TP-User-Data-Header-Indicator | B | Parameter indicating that the TP-UD field contains a Header.
TP-SRR | TP-Status-Report-Request | b | Parameter indicating if the MS is requesting a status report.
bit1 | bit0 | Message type
0 | 0 | SMS-DELIVER (in the direction SC to MS)
0 | 0 | SMS-DELIVER REPORT (in the direction MS to SC)
1 | 0 | SMS-STATUS-REPORT (in the direction SC to MS)
1 | 0 | SMS-COMMAND (in the direction MS to SC)
0 | 1 | SMS-SUBMIT (in the direction MS to SC)
0 | 1 | SMS-SUBMIT-REPORT (in the direction SC to MS)
1 | 1 | Reserved

MTI = 0x01

VP Field Validity Period Format

bit4 | bit3
0 | 0 | TP-VP field not present
1 | 0 | TP-VP field present - relative format

0 | 1 | TP-VP field present - enhanced format
1 | 1 | TP-VP field present - absolute format

On utilise le mode Relative Format : 0x10

RP = 0x10
UDHI = 0
SRR = 0

Donc, au final, le premier octet devra avoir un code : 0b00010001 = 0x11
Message Reference TP-MR
C’est un identifiant différent pour chaque SMS envoyé, il est automatiquement modifié par le mobile. On peut donc le mettre à n’importe quelle valeur.
Destination Address TP-DA
C’est le numéro de téléphone du destinataire. Les numéros de téléphone sont codés un format propre à la norme GSM
Premier octet : type de numéro de téléphone
1 | T y p e - o f - n u m b e r | N u m b e r i n g - p l a n - i d e n t i f i c a t i o n

Type-of-number:
Bits 6 5 4
0 0 0 | Unknown 1)
0 0 1 | International number 2)
0 1 0 | National number 3)
0 1 1 | Network specific number 4)
1 0 0 | Subscriber number 5)
1 0 1 | Alphanumeric, (coded according to GSM TS 03.38 7-bit default alphabet)
1 1 0 | Abbreviated number
1 1 1 | Reserved for extension

Numbering-plan-identification (applies for Type-of-number = 000,001,010)
Bits 3 2 1 0
0 0 0 0 | Unknown
0 0 0 1 | ISDN/telephone numbering plan (E.164/E.163)
0 0 1 1 | Data numbering plan (X.121)
0 1 0 0 | Telex numbering plan
1 0 0 0 | National numbering plan
1 0 0 1 | Private numbering plan
1 0 1 0 | ERMES numbering plan (ETSI DE/PS 3 01-3)
1 1 1 1 | Reserved for extension
All other values are reserved.

Pour notre projet, nous utiliserons un numéro de téléphone international (au cas où le ballon tombe à l’étranger). On configurera donc ce champ à la valeur
0b10010001 = 0x91

Deuxième octet : longueur

Longueur du numéro de téléphone. TP-Protocol-Identifier (TP-PID)
bits | usage

7 6
0 0 | Assigns bits 0..5 as defined below
0 1 | Assigns bits 0..5 as defined below
1 0 | reserved
1 1 | Assigns bits 0-5 for SC specific use

In the case where bit 7 = 0, bit 6 = 1, bits 5..0 are used as defined below 5 .. . .0
000000 | Short Message Type 0
000001 | Replace Short Message Type 1
000010 | Replace Short Message Type 2
000011 | Replace Short Message Type 3
000100 | Replace Short Message Type 4
000101 | Replace Short Message Type 5
000110 | Replace Short Message Type 6
000111 | Replace Short Message Type 7
001000..011110 | Reserved
011111 | Return Call Message
100000..111100 | Reserved
111101 | ME Data download
111110 | ME De-personalization Short Message
111111 | SIM Data download

Nous envoyons un SMS standard (les autres types étant utilisés sur les portables de nouvelles génération), de type 0. Donc ce champ doit être à la valeur : 0b00000000 = 0x00

TP Validity Period TP-VP

C’est la durée de stockage du SMS dans le centre serveur, tant qu’il n’a pas été envoyé.

TP-VP value | Validity period value
0 to 143 | (TP-VP + 1) x 5 minutes (i.e. 5 minutes intervals up to 12 hours)
144 to 167 | 12 hours + ((TP-VP -143) x 30 minutes)
168 to 196 | (TP-VP - 166) x 1 day
197 to 255 | (TP-VP - 192) x 1 week

255 = 58 semaines.

Codage du texte : alphabet 7-bits

Texte original, en ASCII
A7 | A6 | A5 | A4 | A3 | A2 | A1 | A0 | B7 | B6 | B5 | B4 | B3 | B2 | B1 | B0 | I7 | I6 | I5 | I4 | I3 | I2 | I1 | I0
Caractère 0 | | | | | | | | Caractère 1 | | | | | | | | Caractère 7

En codage 7 bits

B0 | A6 | A5 | A4 | A3 | A2 | A1 | A0 | C1 | C0 | B5 | B4 | B3 | B2 | B1 | B0 | I6 | I5 | I4 | I3 | I2 | I1 | I0 | H6
Caractère 0 | | | | | | | | Caractère 1 | | | | | | | | Caractère 6

2.5.2.7. Création d’un programme pour tester le mode PDU

Pour mieux prendre en main la composition en mode PDU, nous avons écrit un programme Java permettant la communication avec le mobile au moyen du port infrarouge. Ce programme permet d’envoyer des commandes AT et donc un message SMS. Il est beaucoup plus souple à utiliser qu’un codage directement sur le PIC, avec à chaque fois les longues étapes de compilation / programmation.
Il s’est montré indispensable pour comprendre les champs des messages PDU et le codage 7-bits de l’alphabet.
Le code source est donné en annexe.
2.5.2.8. Contrôle de l’alimentation

Certains des mobiles que nous avons utilisés s’allument dès application d’une tension sur leur connecteur d’interface. En revanche, le modèle retenu reste éteint lors de l’envoi des commandes AT ou lors d’une alimentation extérieure.
Comme on souhaite contrôler l’allumage/extinction du portable, la seule solution restante est de court-circuiter le bouton poussoir du clavier utilisé pour l’allumage. N’étant pas encore sûr du moyen à utiliser, nous plaçons deux relais sur la carte PIC qui seront ensuite utilisés selon le modèle du portable retenu.
2.5.2.9. Microcontrôleur

On réalise un montage standard autour d’un PIC 16F876. Comme les opérations à effectuer ne sont pas très complexes, on peut choisir n’importe quelle fréquence de fonctionnement. Pour limiter la consommation, on prend 10,5984MHz (le premier qu’on ait trouvé dans le tiroir). On ajoute un convertisseur de niveau MAX233 pour interfacer le PIC avec un port série RS232. L’utilisation d’un terminal sur PC s’avère très pratique pour mettre au point le logiciel, surtout que le compilateur gère la fonction ‘printf(…)’ vers le port série. Deux jumpers permettent de diriger les communications selon 3 modes de fonctionnement :

- PIC – GSM : normal
- PIC – RS232 : essais logiciels
- GSM – RS232 : essais mobile
Une led dite « led vie » sert de témoin de bon fonctionnement. Selon son état (fixe, clignotante) on peut connaître dans quelle phase est le programme.
2.5.2.10. Logiciel embarqué

La programmation est réalisée en C.
Remarques : le compilateur optimise parfois à tort, et on a notamment rencontré ce problème :
{
…
i2c_read() ; // Attente d’un octet sur le bus I2C
}
qui aurait du se traduire par un test du flag de réception d’un octet, est en fait compilé en nop. Pour obtenir la bonne compilation, il faut utiliser une affectation, le compilateur comprend alors que l’instruction est importante.

{
…
t = i2c_read() ;
}
fonctionne bien.
Par la suite, on s’est passé au maximum des fonctions du compilateur pour faire des accès directs aux registres du PIC.
Pour nos essais, nous n’avons pas utilisé le critère ‘être dans le dernier kilomètre’ pour envoyer des SMS. Cela pourra se faire avec un simulateur de trame GPS, en cours de développement.

### 2.5.3. Tests

2.5.3.1. Tests unitaires

Nous avons réalisé des petits programmes qui testent le bon fonctionnement de chaque périphérique du pic (led vie, relais, port série, bus I2C).

2.5.3.2. Communications GSM – PIC

Espion sur port série :

AT+CMGF=0
OK
AT+CSMS=0
+CSMS: 1,1,1

OK
AT+CMGS=63
>
07913386094000F011C40B913386905060F60000FF37CC305D07A2E19C34998B76C3D14 00DE6DB
AD03C160B2222CE7BAD56C375023C8A6836030180CD6063562331DACA69BD500

+CMGS: 187

OK

### 2.5.4. Conclusion

Nous pouvons envoyer avec succès des SMS contenant la position GPS du ballon. Il reste encore quelques modifications à faire sur le logiciel pour prendre en compte les conditions d’envoi du SMS (dernier kilomètre, en descente). Nous devons aussi régler le problème de l’alimentation du mobile, mais nous préférons le faire après la présentation, par crainte d’endommager le mobile (il faut en effet souder au niveau du bouton marche/arrêt, sur des pistes assez fragiles).

## 3. Alimentations

## 3.1. Présentation

L'alimentation d'un ballon est la partie essentielle pour le succès d'un projet ballon. Elle est loin d'être évidente et peut mener à l'échec d'un projet. Dans un ballon, elle est soumise à plusieurs contraintes, que l'on a pu rencontrées :

– La masse limitée du ballon, qui oblige à limiter le nombre de piles et à surveiller le rendement

– La CEM, alimenter de l'électronique d'instrumentation et un émetteur à partir de la même source n'est pas évident.

– Les conditions atmosphériques, les caractéristiques des piles n'étant déjà pas trop documentées à température ambiante, elles sont inconnues aux basses températures.

## 3.2. Bilan électrique

### 3.2.1. Besoins

Carte | Tensions | Consommation | Capacité requise, vol de 3,5h
PIC1 | 4,5 à 5,5V | 50mA | 1,1 A.h
GPS | 4,75 à 5,2V Ripple 50mV c/c | 250mA
Modulateur FSK | 12V | 20mA
Environnement | +8V -8V | 50mA | 200 mA.h
Geiger | 9V | 50mA
Emetteur | 9 à 12V | 250mA | 1 A.h

### 3.2.2. Ressources

Autant de piles 4,5 que l’on veut. C’est une limite que l’on s’impose, justifiée par l'expérience de la tenue des ces piles au froid (en particulier des Duracell, seules piles du commerce à être presque correctement documentées). Mais c’est vrai qu’on sera limité sur les tensions disponibles en entrée (4,5V, 9V, 13,5V).

## 3.3. Synthèse

La carte PIC (avec le module GPS) est la plus gourmande en énergie. C’est également celle sur laquelle se trouve toute l’électronique. On choisira donc une alimentation propre est puissante.
Les cartes environnement sont essentiellement en analogique. Elles sont aussi très sensible au bruit, mais consomment peu. Par contre elles nécessitent une alimentation symétrique. On choisira une alimentation symétrique propre.
L’émetteur est un gros consommateur, mais possède son propre régulateur. Il faudra l’essayer avec une alimentation un peu ‘sale’.
Devant l’étendue de toutes les tensions demandées, la carte alimentation fournira les tensions suivantes, les autres étant générées à partir de celles-ci au niveau local.
GND, +12V, -12V, +5V

## 3.4. Conception

### 3.4.1. Contraintes

L’utilisation d’alimentations à découpage, outre l’aspect formateur (jamais réalisées auparavant), offre un excellent rendement et donc une optimisation des piles. On l’utilisera pour les systèmes les plus consommateurs d’énergie. Il s’agit donc du PIC et du GPS.
Toutefois le bruit qu’elles génèrent peut dégrader les performances des cartes alimentées. Pour les cartes les plus sensibles on placera un régulateur linéaire LDO en sortie de l’alimentation à découpage. Ces cartes seront donc pourvues localement d’un LDO qui fournira également les tensions demandées par les circuits.
On essaiera d’utiliser au maximum des combinaisons de piles en série, qui évitent l’autodécharge d’une pile dans une autre.

### 3.4.2. Régulation à découpage

Alimentation processeur/GPS +5V 400mA, 5V :
fréquence de découpage : 200 kHz. Inductance propre : 100µh
Energie stockée : ½.L.I²
Régulation: 5V, rendement 85%, Imax=500mA
→ 2,9W.
Pour un cycle, E0 = 2,9/200.000 = ½ LI² → Il=550mA

Alimentation +12V/-12V

Piles, 9V; Step Up; Inverter

En utilisant une source de 9V, on utilisera uniquement des convertisseurs step-up. En utilisant une source de 13,5V et convertisseur Step-Down, on peut imaginer que la température et l’usure des piles puissent faire baisser la tension en dessous de 12V, et donc le mode step-down du convertisseur ne pourrait plus fonctionner.
Une configuration Sepic de l’alimentation à découpage aurait permis un fonctionnement dans les deux cas, mais elle est plus complexe et pas vraiment justifiée.

Piles,
13,5V | Step Down | +5V

## 3.5. Réalisation

### 3.5.1. Prototype

Pour valider la possibilité d’alimenter les circuits ‘sensibles’ par une alimentation à découpage, on réalise un petit circuit d’alimentation 5V.
Ne pas oublier de bien dimensionner l’inductance ! Le premier essai, où je demandais ambitieusement 1A dans une résistance de puissance, s’est terminé par une fumée malodorante sortant de l’inductance. En regardant de plus près la datasheet, celle-ci ne tolérait qu’une dissipation associée à un courant de 600mA…
Si l'alimentation donnait satisfaction pour la partie logique (aucun problème avec le GPS), ce fut en revanche une catastrophe sur la partie analogique, lorsque l'alimentation marchait (pas à tout les coups).

### 3.5.2. Conclusion

En définitive, la réalisation d'alimentations à découpage s'est soldée par un échec, le bruit en sortie étant trop important pour l'électronique analogique, et la réalisation d'un bon filtrage demandait trop de temps et de moyens.
Nous nous sommes donc tournés vers des régulateurs à découpage tout intégrés, de chez Texas Instruments, auxquels on a ajouté un filtre LC en PI, avec des ferrites sur les lignes d'alimentation.

## 3.6. Bilan de puissance

### 3.6.1. Estimé

### 3.6.2. Mesuré

Batteries | Mesure Alimentation
V (V) | I (A) | P (W) | V | I | P
Kiwi | 13,50 | 0,210 | 2,84
5 | 13,50 | 0,148 | 2,00 | 0,75 | 5,00 | 0,300 | 1,50
-12 | 9,00 | 0,000 | 0,00 | 0,85 | 12,00 | 0,000 | 0,00
12 | 9,00 | 0,111 | 1,00 | 0,60 | 12,00 | 0,050 | 0,60
Tension | Intensité(A) | Puissance (W)
9,00 | 0,11 | 1,00 | 0,17 | 0,391,5A.h
13,50 | 0,36 | 4,84 | 0,54 | 1,251,5A.h
Durée du vol | 3,50

Rendement
conversion

Par pile de 1,5V
(W)

Capacité
requise (A.h)
par pile

Capacité
annoncée
MN1203
500mA

Le bloc de 6 piles 9V est donc doublé.
Pour l'émetteur, on a choisi 9 piles 1,5V comme source exclusive.
Durée de vol | 3,5h
| Courant sortant | Par pile
SANS EMETTEUR
13,5V | 0,38A | Capacité requise | 1,33 A.h
| | Puissance dissipée | 0,57 W
3 piles | par pile 0,13
9V | 0,29A | Capacité requise | 2,35 A.h
| | Puissance dissipée | 1,01 W
6 piles

0

## 4. Télémesures

## 4.1. Emission

L’émission se fait par modulation FSK 600 bauds sur l’entrée externe de l’émetteur KIWI.

## 4.2. Modulation FSK

Les trames sont transmises par modulation FSK avec 2 fréquences clefs à f0=900Hz et f1=1,5kHz, autorisant un débit maximum théorique de 600 bauds.
Le circuit sera basé sur un VCO (Voltage Controlled Oscillator) à XR2206, montage courant dans les clubs spatiaux.


- f0 = 1 / R1.C
- f1= = 1 / R2.C
La datasheet recommande :
- C [1nF, 100µF]
- R [1kohm, 2Mohm]

On fixe C = 100nF, et on trouve
R1 = 11,111kOhm et R2 = 6,667kOhm

## 4.3. Trames télémesures

### 4.3.1. Spécifications

Emission trame GPS : toutes les 5 secondes
Emission température, pression, radioactivité : toutes les secondes
Emission statut général (à définir, reboot, tensions piles, …) : toutes les 10 secondes. Débit 600 bauds pour une meilleure densité de puissance spectrale

### 4.3.2. Protocole

Format de transmission bas niveau

- 600 bauds, format RS232
- 1 bit de start
- 8 bits de données
- 1 bit de stop
- sur modulation FSK 600 bauds 9000/15000.
- Durée de transmission (1 octet de donnée) : 16,7ms

Tolérance sur le baudrate

En négligeant les temps de montées / descentes (qq centaines de nanosecondes), on considère la synchronisation de l’UART de réception sur le front descendant du START.
baudMin = 569
baudMax = 631

### 4.3.3. Format d’encapsulation des trames

- Octets de synchronisation : 0xFF 0xFF 0xAA
- Type de trame (1 octet)
- Données
- Checksum (XOR des données) Types de données
[xxx] : x caractère ascii
1) 5,3%
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
9 | 9 | 1
= ± | - = ±

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
### Baud

### Baud

### Baud

### Baud

### Baud Baud

### Baud

Baud | Baud Baud | Baud

entier signé / non signé : entier binaire MSB first

4.3.3.1. Trame GPS NMEA variante ‘Light’

Trame NMEA non compatible (quoique…), mais beaucoup plus légère.
Avantages : on garde la représentation ‘caractère’, lisible sous un terminal et directement exploitable par le GSM, tout en diminuant la durée totale d’une trame.
On garde le séparateur de chaînes ‘,’.
Offset | Format | Taille (octets) | Description
0 | 0xFF,0xFF,0xAA | 3 | Synchronisation
| 0x91 | 1 | Type de trame (GPS)
| [hhmmss]’,’ | 7 | Heure
| [ddmm]’.’[mmmm]’,’ | 10 | Latitude
| [‘N’/’S’]’,’ | 2 | Hémisphère Nord/Sud (bof…)
| [dddmm]’.’[mmmm]’,’ | 11 | Longitude
| [‘E’/’W’]’,’ | 2 | Secteur Est/Ouest
| [‘0’/’1’]’,’ | 2 | Position valide
| [nn]’,’ | 3 | Nb de satellites utilisés
| [nn]’,’ | 3 | HDOP (partie entière uniquement)
| [aaaaa]’,’ | 6 | Altitude en mètres
| Entier non signé | 1 | Checksum (XOR)
| | 51

Durée : 852 ms (quand même…)

4.3.3.2. Trame expériences

Type de trame : 0x13

Offset | Type | Taille (octets) | Description
0 | 0xFF,0xFF,0xAA | 3 | Synchronisation
3 | 0x13 | 1 | Type de trame (Expériences)
4 | Entier signé | 1 | Température intérieure en °C
6 | Entier signé | 1 | Température extérieure en °C
7 | Entier non signé | 2 | Pression en Pa
9 | Entier non signé | 2 | Nombre de coups Geiger entre deux envois de trame
| Entier non signé | 1 | Checksum

Durée de transmission : 184 ms

4.3.3.3. Trame statut général

Type de trame : 0xB4

Offset | Type | Taille (octets) | Description
0 | 0xFF,0xFF,0xAA | 3 | Synchronisation
3 | 0xB4 | 1 | Type de trame (Statut)
4 | Entier non signé | 1 | Tension 1
5 | Entier non signé | 1 | Tension 2

6 | Entier non signé | 1 | Tension 3
7 | Entier non signé | 1 | Nb d’envois de SMS
8 | | 1 | Checksum

## 4.4. Réception

### 4.4.1. Logiciel de réception

Le logiciel de réception est une application écrite sous Visual C++. Je tiens à remercier Jérôme Hamm pour son code du projet Axelle (CLES-FACIL).
Les données de chaque expérience sont affichées numériquement.


La position GPS est reportée sur un logiciel de cartographie quelconque en utilisant un port série virtuel. Le logiciel de réception reçoit les trames GPS, les encode sous une forme NMEA standard puis les réémet sur un port série virtuel. Un logiciel en shareware boucle ce port série vers un autre port virtuel sur lequel le logiciel de cartographie recevra les trames NMEA. Au départ la gestion du port série virtuel devait être gérée par le logiciel de réception, mais, par manque de temps, il a fallu recourir à un shareware.

Logiciel de réception; Logiciel de cartographie (Mappoint); Boucle de ports séries virtuels; Trame NMEA

## 5. Lâcher du ballon

## 5.1. Cadre du lancement

Une première date de lancement avait été envisagée le 31 juillet 2004 lors de la Rencontre Nationale des clubs Espace 2004 à Flixecourt. La phase de tests de télémesure ayant fait apparaître des dysfonctionnements, le lancement a été reporté au 19 septembre 2004 depuis la base de loisirs de Buthiers. Le lâcher s’est effectué sur le parking et la réception fixe se faisait depuis l’observatoire. Nous disposions d’un système de réception mobile. Une voiture était équipée d’un récepteur AR8200, d’un démodulateur KIWI et du logiciel de réception dédié au ballon ; une seconde voiture était équipée d’un récepteur « Gonzague », d'un onduleur 12V - 220V et du logiciel Keasy.


## 5.2. Récupération du ballon

Les deux voitures était équipées d’un logiciel de cartographie qui permettait de visualiser la position GPS de la voiture et du ballon. L’une a emprunté la nationale, l’autre l’autoroute ; les deux sont arrivées à proximité du point de chute environ 10 minutes après la réception de la dernière trame. La poursuite du ballon a donc été un succès. Son état général est très bon, les cartes n’ont pas bougé, seule l’antenne filaire s’est déformée, entraînant la fin de l’émission des télémesures après l’impact.


## 5.3. Récupération des résultats

Le logiciel KEasy a bien fonctionné tout au long du vol et a aidé à la récupération du ballon. Malheureusement, les données reçues n’étant pas enregistrées (ou étant effacées lors d'un nouveau lancement), le logiciel ne nous a été d’aucune utilité pour l’exploitation des résultats.
En raison d’un problème de réception avec le récepteur mobile de la deuxième voiture, la première phase de vol n’a pas été reçue mais l’enregistrement des données a pu être correct à partir de la fin de la montée et jusqu’à l’atterrissage, ce qui permis de localiser le ballon au sol avec précision.
Le système qui était considéré le plus fiable, à savoir la station de réception fixe, a rencontré de nombreux problèmes encore inexpliqués (connecteur d'antenne défaillant ?). L'erreur principale a été de partir suivre le ballon en voiture sans avoir regardé le bon fonctionnement de la station fixe (qui n'était qu'à 10 minutes du parking). Comme la personne s'occupant de la station fixe n'était pas membre du projet, elle n'a pas noté le comportement anormal de la réception. Il s'agit là de la plus grosse erreur commise sur ce projet.

Illustration 11: Nico l'a vu,, Manu l'a entendu

## 6. Exploitation des résultats

## 6.1. Traitement des données

Toutes les données sont exportées vers une structure unique sous Matlab, qui permet une manipulation plus simple qu’Excel.

## 6.2. Données générales sur le vol

Altitude maximale : 21 738 m
Durée de vol : 1h58 min (ballon beaucoup gonflé) Distance directe parcourue :

## 6.3. Atmosphère

### 6.3.1. Température

6.3.1.1. Température intérieure :


La nacelle s’est refroidie pendant toute la durée de la montée à partir de 8000m, puis s’est réchauffée en descente, en dessous de 6000m. La température de la nacelle est restée toujours très supérieure à celle de l’atmosphère durant quasiment tout le vol. Au-delà de 800m, la température de l’atmosphère standard est inférieure à 12°C, température minimale atteinte par la nacelle. Il y a donc eu un refroidissement continu de la nacelle par conduction thermique. Les hausses de température observées dans les altitudes basses sont sûrement dues aux transferts de chaleur par rayonnement. La hausse due au rayonnement apparaît plus tardivement lors de la descente, car la vitesse de descente est plus importante que celle de montée à ces altitudes.

Illustration 12: Température intérieure

L’amplitude du refroidissement a été plus importante durant la montée, car la vitesse ascensionnelle y est moins importante, donc les échanges thermiques durent plus longtemps.

6.3.1.2. Température extérieure


La température extérieure est conforme au modèle standard, même si la température minimale reste assez élevée. La différence de température entre la montée et la descente, à même altitude, s’explique par l’inertie thermique des capteurs.

### 6.3.2. Radioactivité

Les données transmises sur la radioactivité sont toutes entachées d'une erreur !!
En effet, le programme compte le nombre d'impulsions reçues entre 2 envois de trame. Les deux envois devaient se faire à 3 secondes d'intervalles, ce qui permettait de retrouve le nombre de coup par seconde. Cependant, peut être à cause de problèmes d'interruptions sans priorité, cette période est beaucoup plus aléatoire, de 3 à 5 secondes... Par suite, il est impossible de remonter au début de dose de manière fiable.
On donne tout de même les graphes des valeurs reçues, en nombre de coups entre deux envois, sans connaître précisément la période d'envoi (3 secondes à 80%)

Illustration 13: Température extérieure



On corrige ces erreurs en rejetant systématiquement toutes les périodes d'acquisitions différentes de 3 et 5 secondes, à l'aide d'un petit script Matlab. Une centaine de mesures sont ainsi éliminées. Les mesures restantes sont exactes.

Valeurs corrigées :Les dernières mesures (chute brutale) ne sont pas en prendre en compte et sont lerésultat du filtrage.
On observe un maximum, probablement le pic découvert par Pfotzer en 1936, aux alentours de 15-20 km.
Avec la relation théorique 1 cps = 0,46µSv/h, le débit de dose maximum est de 3,9 µSv/h, autour de 17km d'altitude.

## 6.4. Trajectoires

### 6.4.1. Vitesse ascensionnelle


On remarque une vitesse de montée bien constante, autour de 5 m/s, et une vitesse de descente qui suit bien celle de la masse volumique de l'air.

Illustration 14: Vitesse ascensionnelle en altitude

### 6.4.2. Trajectoire sol

Trajectoire du ballon, ascension en rouge et descente en orange
Trajectoire de la voiture, en vert. Le petit crochet à Nemours, sur un parking de McDo, a permis de configurer convenablement le récepteur pour recevoir toutes les télémesures. Le ballon était alors au dessus de Chéroy.


## 7. Bilan

## 7.1. Organisation du projet

### 7.1.1. Problèmes techniques

Les plus gros problèmes techniques sont venus de la réception des télémesures. En particulier, l'utilisation de 3 trames différentes, envoyées avec des périodes différentes et surtout sans transmettre une référence de temps (heure, numéro de trame) fut une erreur énorme, à la limite du compréhensible !
Un autre point qui a pu sembler délicat est celui des alimentations, peut être dimensionnées un peu juste.
L'absence totale d'envois de SMS par le ballon le jour du vol reste un mystère. Ils sont peut être à relier avec la carte SIM du téléphone, utilisée maintenant par Nicolas et qui présente des problèmes répétés (impossible de trouver la borne la plus proche, redirection immédiate vers le répondeur même en cas de bonne couverture, etc...)

### 7.1.2. Carte environnement

L'abandon de la carte environnement, à quelques jours du lâcher et suite à des problèmes d'interférences radiofréquences (probablement des couplages entre les champs émis par antenne, et les boucles créées par les capteurs, avec des impédances communes), ou par retour de HF sur les alimentations reste un point décevant du ballon, surtout vu le soin particulier apporté à cette carte, de sa conception (y compris CEM !) jusqu'à son étalonnage. Les couplages par impédance commune seront à surveiller de plus près la prochaine fois, et l'utilisation de liaisons différentielles sera à privilégier.

## 7.2. Résultats

### 7.2.1. International Astronautical Congress

A la suite d'un appel à présentations de l'ESA pour le Congrès International d'Astronautique, le ballon OKOUR a été retenu, et Claire a été choisie pour présenter le projet à Vancouver (Canada).

### 7.2.2. Télémesures

Globalement, et après de très longues heures pour dater et identifier les trames reçues par la seule des 3 stations ayant enregistrée les données, les résultats des télémesures sont assez satisfaisants.

## 7.3. Conclusion

Le ballon a occupé une place importante pour nous tous et durant toute une année, en détachement quasi-compet des études. L'organisation de projet, les connaissances théoriques acquises, les difficultés levées et le savoir-faire développé marquent déjà le projet d'une très grande réussite.
Après de nombreuses péripéties, le ballon a pu prendre son envol. Malgré quelques difficultés sur la fin, lors de la réception et l'analyse des télémesures, les résultats obtenus sont intéressants et en tout cas confirment le succès technique du projet.
La sélection du projet Okour par l'ESA et sa présentation à Vancouver, lors de l'IAC 2004, ont été la consécration finale du projet.

## 8. Remerciements

Nos remerciements vont en premier au CNES et à Planète Sciences, pour l'occasion unique qu'ils offrent aux jeunes. Nous remercions également l'ESA et l'IAF qui nous ont permis de présenter le ballon à l'International Astronautical Congress de Vancouver.
Plus particulièrement, nous souhaitons remercier chaleureusement:

– Les experts divers en électronique, informatique et autres :
Gérard Auvray, Nicolas Chaléroux, Jérôme Hamm, Manu Jolly, Francis Lésel, Etienne Maier, Michel Maignan

– Aux permanents et amis du mercredi soir
Etienne, Vincent, Laurent et les autres

– Aux profs de Supélec qui nous ont soutenus :
M. Benabes et M. Gauthier

– Aux participants de la chasse au ballon et du lâcher Manu, Nico, Caroline, La famille Costy, La famille Guérad

## 9. Annexes

## 9.1. Expérience GSM

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

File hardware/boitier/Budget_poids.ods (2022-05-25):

 | Prévu | Réalisé 30/03
 | poids (g) |  | polystyrène 30mm |  | 0,105 | g/cm²
Nacelle (30*30*22) Couvercle (30*30) | 604,00 | 442
Couvercle (30*30)
carte sigfox BTS | 56,00
Pack 8 piles & dc-dc | 147,00
Gopro & câble | 194,00 | 169 | Détail Nacelle
Accu & chargeur & APRS | 338,00 | 384 |  | largeur (cm) | hauteur (cm) | nb | poids (g)
GPS | 94,00 |  |  |  |  |  |  | 42 | 126 | 0,333333333333333 | 24
panneaux solaire | 120,00 |  | petit côté | 24 | 25 | 2 | 126,00
carteTTGO | 30,00 |  | grand côté | 30 | 25 | 2 | 157,50
antennes | 42,00 | 43 | fond | 24 | 24 | 1 | 60,48
 |  |  | couvercle | 30 | 30 | 1 | 94,50
 |  |  |  |  |  | Total Polystyrene | 438,48
 |  |  |  |  |  | Colle | 165,00
Total | 1625,00 | 1038
marge | 175,00

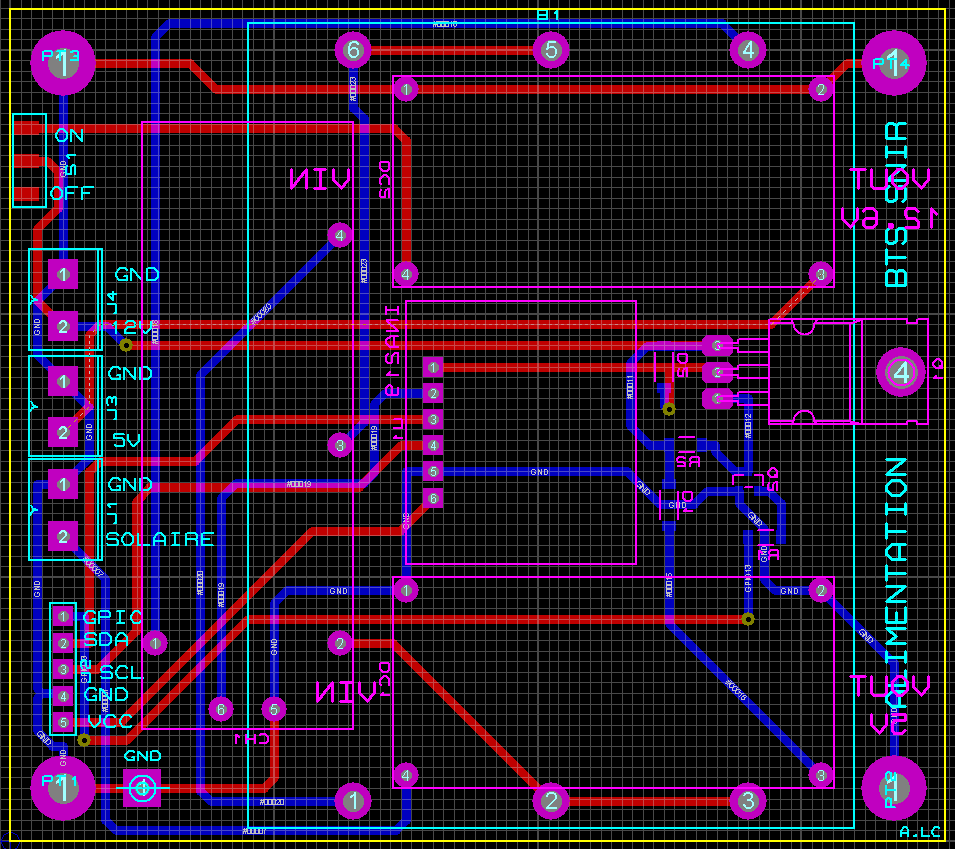
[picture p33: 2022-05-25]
hardware/Alimentation/alim3d_2.png

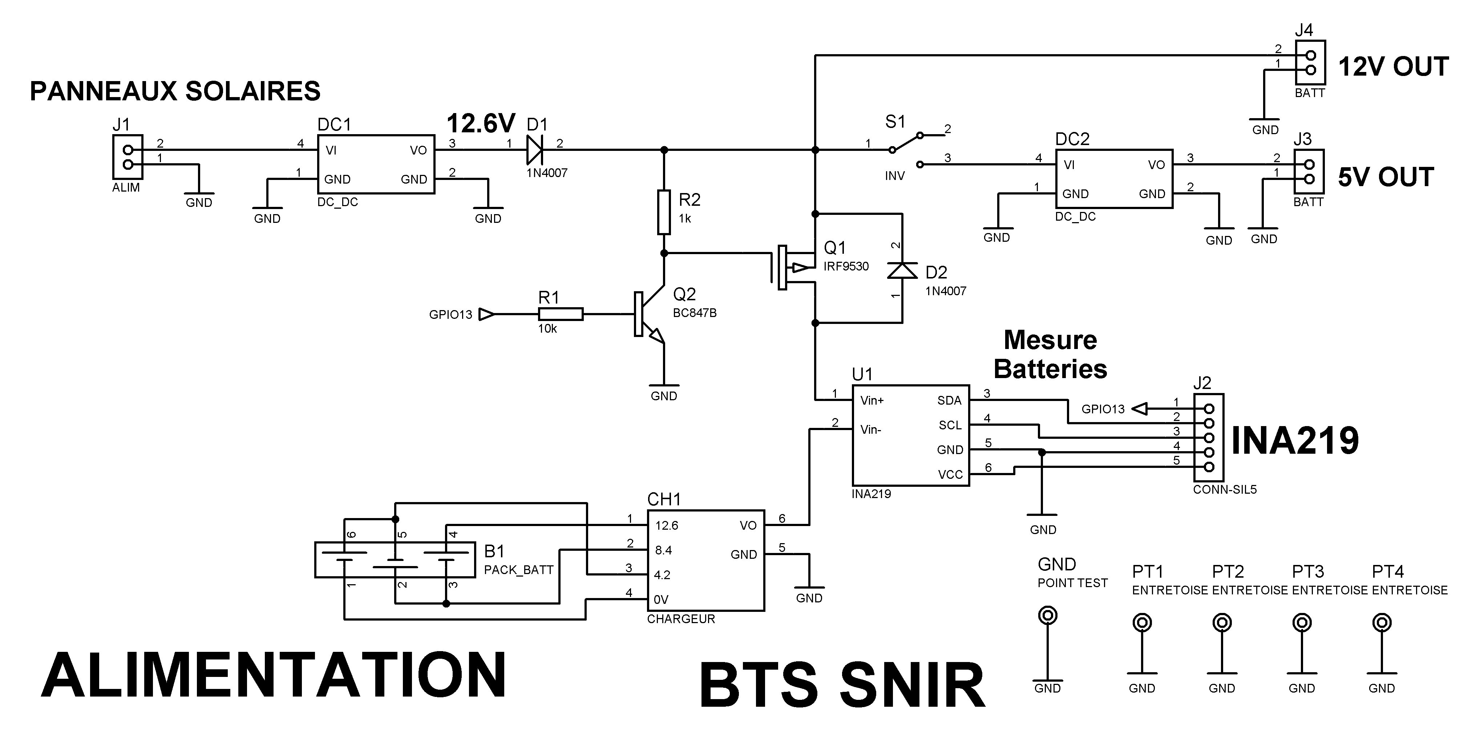
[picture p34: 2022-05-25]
hardware/Alimentation/alim2022sch.png

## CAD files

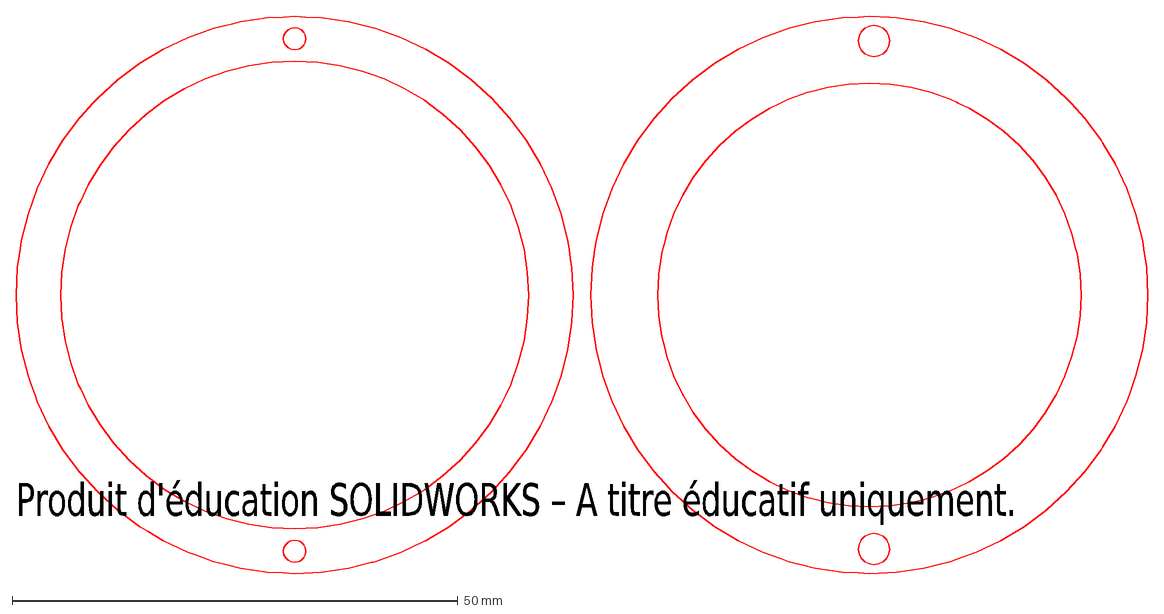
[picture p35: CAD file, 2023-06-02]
hardware/boitier/bague_objectif.DXF
Produit d'éducation SOLIDWORKS – A titre éducatif uniquement.

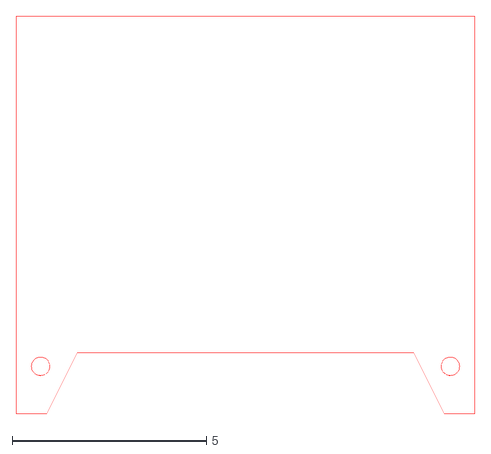
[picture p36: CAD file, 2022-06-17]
hardware/boitier/côté_pieds.dxf
11.8 x 10.2

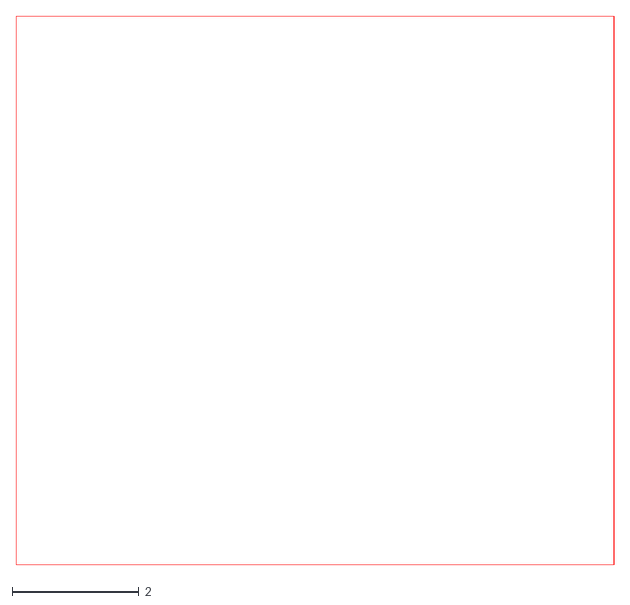
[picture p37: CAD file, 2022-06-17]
hardware/boitier/Petit_côté.dxf
9.45 x 8.66

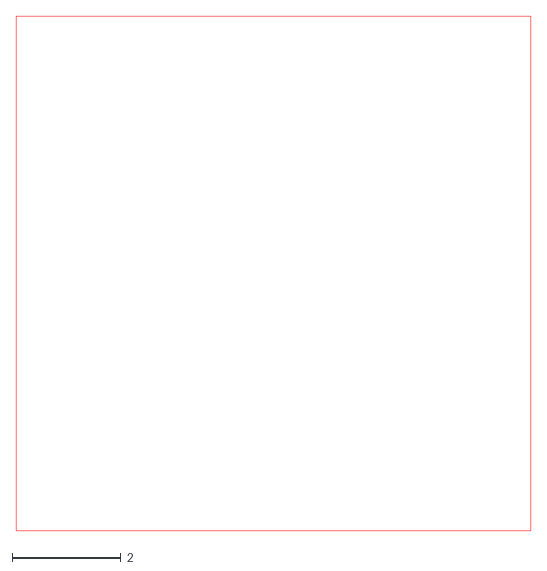
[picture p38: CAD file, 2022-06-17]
hardware/boitier/Fond.dxf
9.45 x 9.45

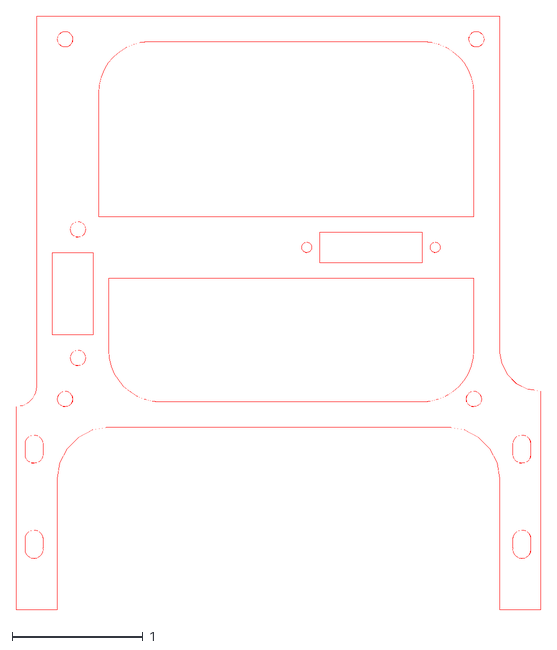
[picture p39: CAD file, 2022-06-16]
hardware/boitier/plaque_intermédiaire_CarteSD_GPS.dxf
4.02 x 4.55

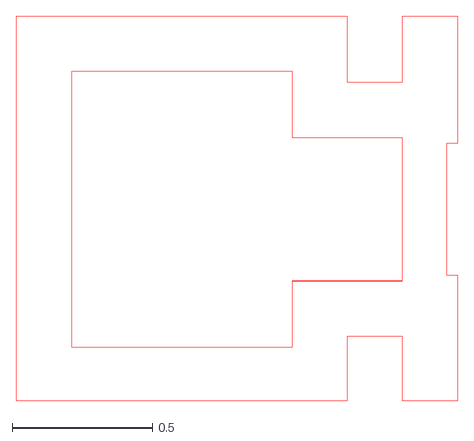
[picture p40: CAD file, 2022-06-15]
hardware/boitier/equerre Lora.dxf
1.57 x 1.37

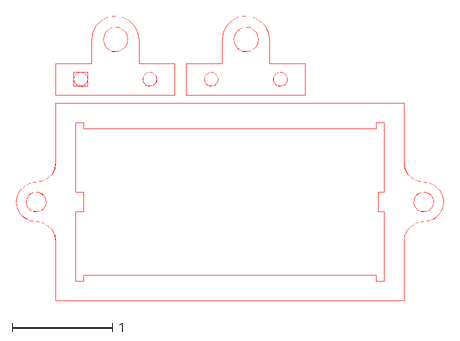
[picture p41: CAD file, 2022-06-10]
hardware/boitier/support_antenne_batterie.dxf
4.25 x 2.83

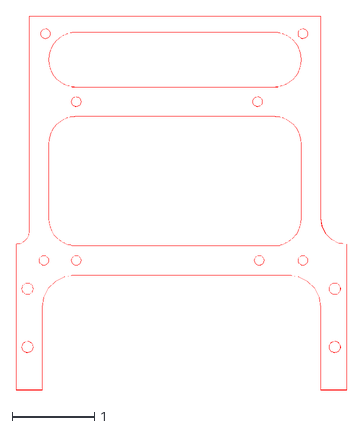
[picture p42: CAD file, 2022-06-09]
hardware/boitier/Plaque_Sigfox_LoRa_renforce.dxf
4.02 x 4.55

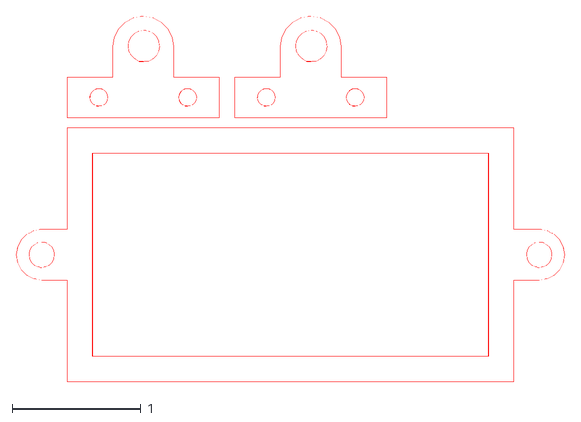
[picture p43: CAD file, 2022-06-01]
hardware/boitier/support_antenne.dxf
4.25 x 2.83

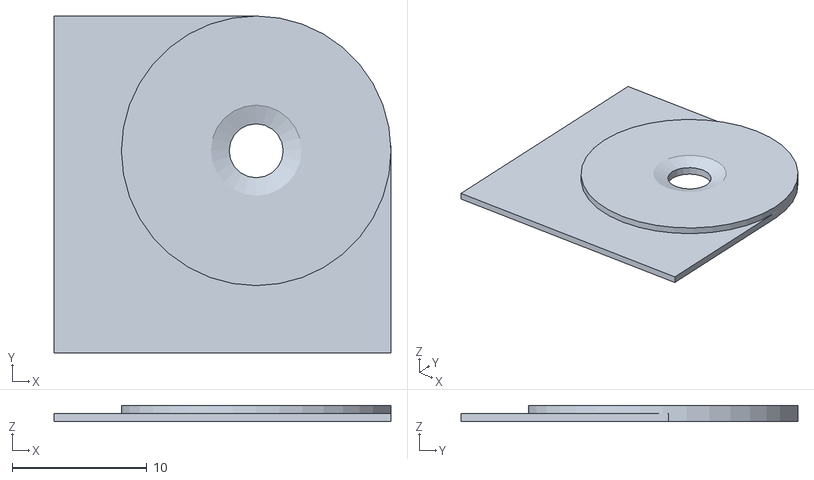
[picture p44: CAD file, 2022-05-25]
hardware/boitier/Coin_nacelle.stl
25.0 x 25.0 x 1.20

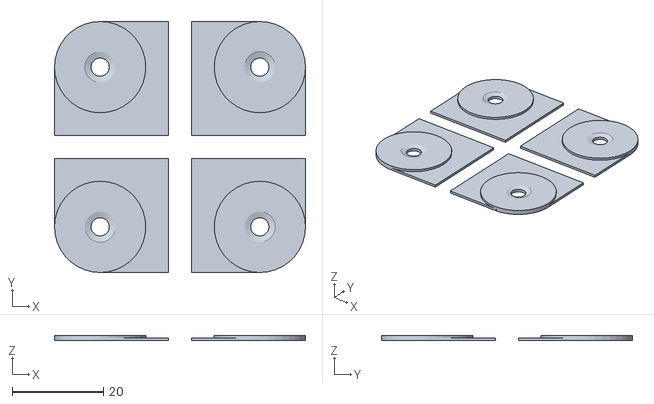
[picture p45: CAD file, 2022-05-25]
hardware/boitier/Coins_nacelle.stl
55.0 x 55.0 x 1.20

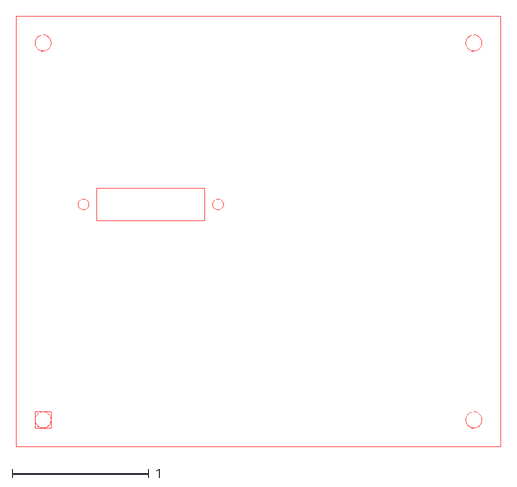
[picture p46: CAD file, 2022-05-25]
hardware/boitier/plaque Ballon.dxf
3.54 x 3.15

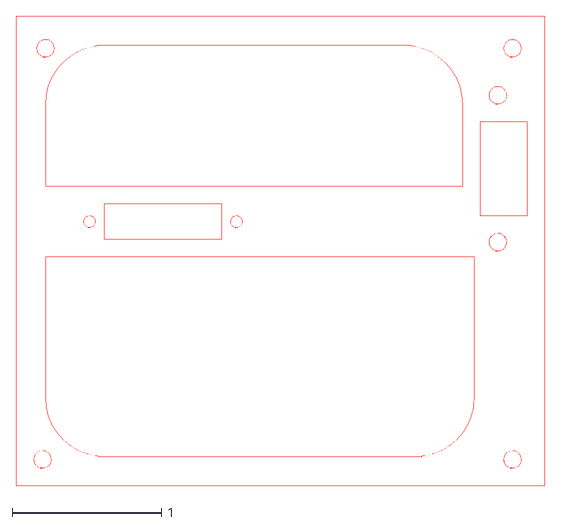
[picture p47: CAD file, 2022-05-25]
hardware/boitier/plaque_intermédiaire_ballon.dxf
3.54 x 3.15

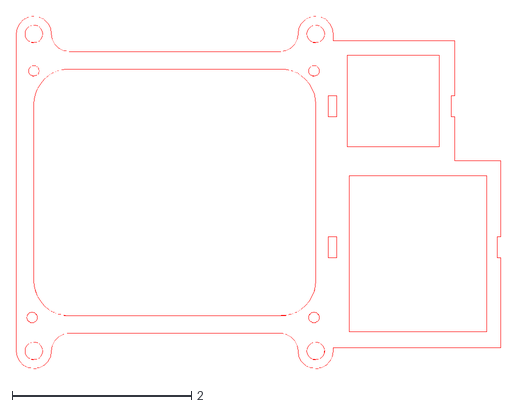
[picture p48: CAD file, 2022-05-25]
hardware/boitier/plaque_couvercle.dxf
5.41 x 3.94

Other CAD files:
hardware/boitier/Rondelle.dxf
hardware/boitier/Gopro_avant2.dxf
hardware/boitier/Plaque_Sigfox_Lora.dxf
hardware/boitier/calage.dxf
hardware/boitier/Coins_nacelle.dxf

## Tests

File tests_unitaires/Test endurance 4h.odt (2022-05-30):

# Test endurance 4h

## Objectif du test

Vérifier la tenue des batteries sur une période de 4h

Vérifier la transmission des datas

Lundi 30 Mai 2022

F4KMN-13 carte APRS

- 09h50 batterie 12,4 V 99% courant -214 mA Wifi enable
- 10h00 batterie 12,4 V 98% courant -170 mA Wifi disable
- 10h30 batterie 12.3 V 95% -164.2 mA
- 11h00 batterie 12.3 V 92% -176.6 mA
- 11h30 batterie 12.2 V 90% -174.4 mA
- 12h00 batterie 12.2 V 87% -175.4 mA
- 12h30 batterie 12.1 V 84% -173.2 mA
- 13h00 batterie 12.1 V 81 % -177.2 mA
- 13h30 batterie 12.0 V 78 %-169.3 mA
- 14h00

F4KMN-11 Carte LoRa

- 10h19 batterie 4,09V -98 mA
- 10h30 batterie 4,08V -112 mA
- 11h00 batterie 4,07V -102 mA
- 11h30 batterie 4,06V -99 mA
- 12h00 batterie 4.05V -100mA RSSI:-68 dBm
- 12h30 batterie 4.05V -99mA RSSI:-62 dBm
- 13h00 Batterie 4.03V -105mA RSSI:-68 dBm
- 13h30 Batterie 4.02V/-105mA RSSI:-68 dBm
- 14h00

C50EE9 Carte Sigfox

- 10h02 Message reçu 1625
- 10h30 Message reçu 1639
- 11h00 Message reçu 1654
- 11h32 Message reçu 1670
- 12h00 Message reçu 1684
- 12h30 Message reçu 1699
- 13h00
- 13h30
- 14h00

Conclusions :

Pendant ce test nous avons rencontré les problèmes suivants:

igate LoRa était dans l'état TCP disable, un reset a permis de la redémarrer.

Des messages Sigfox ne sont pas reçus par la station

On peut aussi voir que le LQI est qualifié de limit par l'opérateur Sigfox.

Pour rechercher la cause du problème

Nous avons changé l’émetteur et mis l'antenne SNOC cela fonctionne 5/5

On remet l'antenne 868 de la nacelle les messages ne ne passent plus.

Je remets l'antenne snoc ça fonctionne à nouveau.

Le problème était dû au petit câble de raccordement IPX SMA.

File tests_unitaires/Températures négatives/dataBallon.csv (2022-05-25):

Time | Nb_Sat | Latitude | Longitude | Altitude | Temp_Int | Temp_BME | Temp_Ext | Pression | Humidité | Dose_uSvh | Cpm | U_batt | I_batt | Charge_batt
09:06:05 | 8 | 48.010033 | 0.206535 | 90.7 | 6.2 | 24.2 | 20.2 | 1000.8 | 33.0 | 0.0 | 0.0 | 12.3 | -12.6 | 2687.1
09:06:15 | 9 | 48.010052 | 0.206527 | 94.3 | 6.9 | 22.7 | 20.2 | 1000.7 | 34.7 | 0.0 | 0.0 | 12.3 | -12.7 | 2687.1
09:06:25 | 9 | 48.010052 | 0.206485 | 93.9 | 7.4 | 21.6 | 20.0 | 1000.7 | 36.1 | 0.0 | 0.0 | 12.3 | -12.5 | 2687.0
09:06:35 | 9 | 48.010052 | 0.206485 | 93.8 | 8.0 | 20.7 | 20.0 | 1000.7 | 38.0 | 0.1 | 3.0 | 12.2 | -80.8 | 2686.9
09:06:45 | 9 | 48.010040 | 0.206478 | 93.7 | 8.5 | 20.0 | 19.5 | 1000.7 | 39.6 | 0.1 | 3.6 | 12.2 | -82.1 | 2686.7
09:06:55 | 9 | 48.010044 | 0.206505 | 94.8 | 9.0 | 19.4 | 19.2 | 1000.7 | 38.9 | 0.1 | 4.0 | 12.2 | -122.8 | 2686.5
09:07:05 | 7 | 48.010044 | 0.206533 | 95.7 | 9.4 | 19.0 | 19.8 | 1000.7 | 40.0 | 0.1 | 3.4 | 12.2 | -117.9 | 2686.1
09:07:15 | 8 | 48.010033 | 0.206562 | 96.9 | 9.8 | 18.6 | 20.0 | 1000.7 | 40.0 | 0.1 | 3.7 | 12.2 | -119.3 | 2685.8
09:07:25 | 8 | 48.010029 | 0.206562 | 97.4 | 10.1 | 18.4 | 20.0 | 1000.6 | 41.1 | 0.1 | 3.3 | 12.2 | -117.8 | 2685.5
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

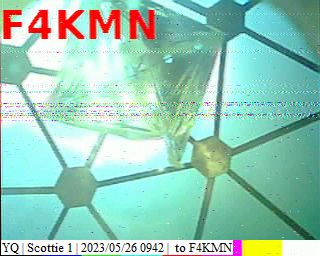
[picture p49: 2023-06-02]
lancement_1_Juin_2023/tests_camera_sstv/polar devant camera avec lunettes.jpg

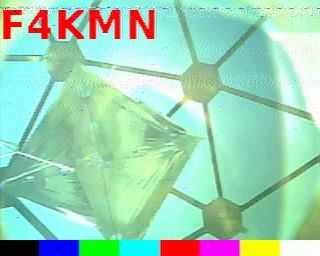
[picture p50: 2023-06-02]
lancement_1_Juin_2023/tests_camera_sstv/polar avec lunettes refecteur.jpg

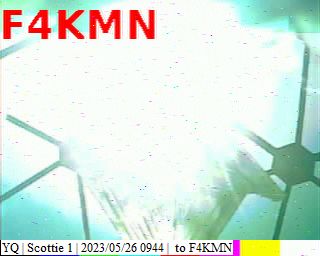
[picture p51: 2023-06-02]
lancement_1_Juin_2023/tests_camera_sstv/polar avec lunettes refecteur soleil.jpg

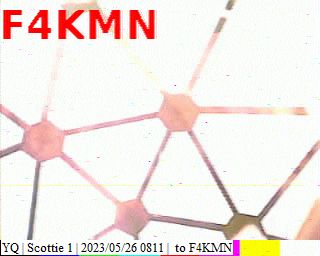
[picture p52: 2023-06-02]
lancement_1_Juin_2023/tests_camera_sstv/polar sans lunettes.jpg

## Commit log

2022-05-31 add antenne
    [support_antenne.dxf]
2022-06-04 add carte lora
    [call_ballon_lora_2022.ods]
2022-06-07 add data format csv
    [dataBallonAPRS.csv, dataBallonSigfox.csv]
2022-06-07 add vidéo éclatement
    [dataBallonAPRS.ods]
2022-06-08 update compte rendu
    [dataBallonAPRS.ods]
2022-06-09 add plaque lora renforcée
    [Plaque_Sigfox_LoRa_renforce.dxf]
2022-06-10 improve support antenne & batterie
    [support_antenne_batterie.dxf]
2022-06-13 add plaque intermédiaire SD GPS
    [plaque_intermédiaire_CarteSD_GPS.dxf]
2022-06-15 update plaque fixation ttgo
    [equerre Lora.dxf]
2022-06-16 update plaque intermédiaire SD GPS
    [plaque_intermédiaire_CarteSD_GPS.dxf]
2022-06-17 add boitier nacelle
    [Fond.dxf, Petit_côté.dxf, côté_pieds.dxf]
2023-06-02 add doc
    [bague_objectif.DXF, mesures aprs.ods]
2023-06-07 add Data 2023
    [donnees 2023 - Prof.xlsx, donnees 2023.xlsx, mesures aprs.ods]
2023-06-07 add dataBallon Carte SD 2023
    [dataBallon.csv]
